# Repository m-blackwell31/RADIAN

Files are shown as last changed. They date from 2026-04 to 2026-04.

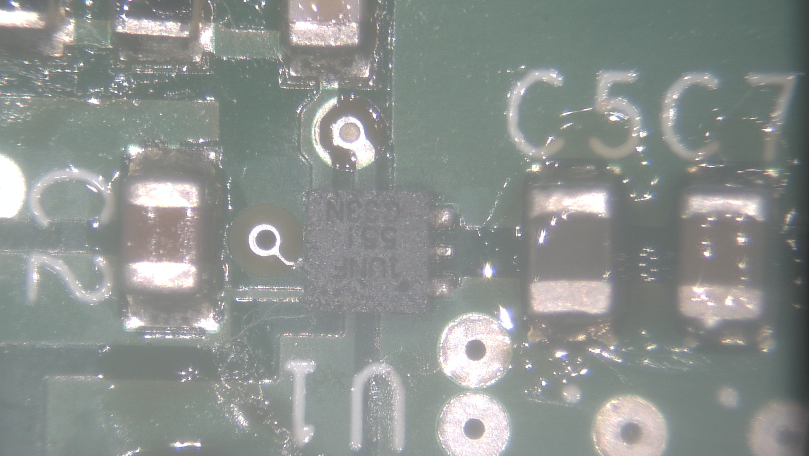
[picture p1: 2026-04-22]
GoogleDrive/physical/power_system/Solder Inspection/IMG00004.JPG

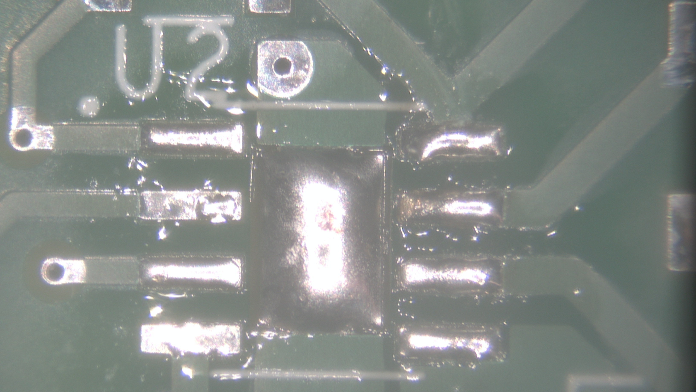
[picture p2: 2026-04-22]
GoogleDrive/physical/power_system/Solderability/IMG00003.JPG

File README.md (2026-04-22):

# RADIAN — Radar-Based Fall Detection System

## Overview

RADIAN is a human fall detection system developed for the Texas A&M University ECEN 403/404 Capstone Course. The system uses a mmWave radar sensor combined with machine learning algorithms to detect falls in real time and alert caregivers via a mobile app notification.

---

## Repository Structure

```
/RADIAN
├── fall_detector/        # ML models (.pkl), fall detector scripts, training code
├── MobileApp/            # Flutter/Dart app (Gotify alerts, fall log, login screen)
├── RADIAN_Data/          # mmWave data collection, CNN model, radar testing scripts
├── RADIAN_Physical/      # PCB design (Altium), CAD enclosure, power system docs
├── RADIAN_Radar/         # AWR6843ISK config (config3.cfg), mmwave_run6.py, requirements
└── GoogleDrive/          # Project documentation, presentations, and reports
    ├── docs/             # FSR, ICD, ConOps, final report, validation plan, budget
    ├── presentations/    # All 403 and 404 status update and demo presentations
    ├── data/             # Demo videos, pipeline diagrams, ML documentation
    ├── physical/         # Power board validation, datasheets, solder inspection photos
    ├── wireless/         # Raw radar testing data (.ndjson files) — falls and non-falls
    └── logo/             # RADIAN logo
```

---

## System Description

RADIAN uses a Texas Instruments AWR6843ISK mmWave radar sensor mounted at an elevated position to monitor a room. Point cloud data is streamed over UART to a Raspberry Pi, where a trained ExtraTrees machine learning classifier determines in real time whether a fall has occurred. Upon detection, a buzzer (GPIO27) alerts locally, and a push notification is sent to the caregiver's mobile app via Gotify.

### Key Components

| Component | Description |
|---|---|
| TI AWR6843ISK | mmWave radar sensor |
| Raspberry Pi | Main compute module |
| AP64501 | Synchronous buck converter |
| MP2615 | Li-ion battery charger IC |
| S-8252AAO | 2-cell battery protection IC |
| 2S2P 7,000 mAh LiPo | Battery pack (~3h 45m runtime) |
| GPIO27 Buzzer | Local fall alert |
| Flutter Mobile App | Caregiver notification app |

---

## Team

**Texas A&M University — ECEN 403/404 Capstone, Spring 2026**
Team 60 — RADIAN

| Name | GitHub |
|---|---|
| Matthew Blackwell | m-blackwell31 |
| Wyatt Johnson | ANDYSALAD1 |
| Mitch Hoffman | hoffmanmitchell |

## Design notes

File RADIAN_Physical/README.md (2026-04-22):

# RADIAN — Physical Subsystem

## Overview

This directory contains all physical design files for the RADIAN fall detection system, including the enclosure, PCB mounting hardware, and battery/component layout. The physical subsystem houses the Raspberry Pi compute module, mmWave radar sensor, power electronics, and buzzer in a compact, mountable enclosure.

---

## Directory Structure

```
/physical
├── CAD/
│   ├── enclosure.SLDPRT         # SolidWorks enclosure part file
│   ├── enclosure.SLDASM         # SolidWorks assembly file
│   └── drawings/                # Exported engineering drawings (PDF)
├── PCB/
│   ├── RADIAN.PrjPcb            # Altium project file
│   ├── Schematics/              # Schematics
│   ├── RADIAN.PcbDoc            # Board layout
│   ├── BOM.xlsx                 # Bill of materials
│   └── Gerbers/                 # Fabrication output files
└── README.md
```

---

## Enclosure

- Designed in **SolidWorks**
- Houses the Raspberry Pi, mmWave sensor, battery pack, and power board
- Mounting features for PCB standoffs and sensor window cutout
- Export formats: `.SLDPRT`, `.SLDASM`, PDF drawings

---

## PCB Design

- Designed in **Altium Designer**
- Includes power regulation (buck converter), MP2615 battery charger, and S-8252 protection IC 
- Battery: 2S2P 7,000 mAh LiPo pack (~3h 45m runtime under ~1,500 mA load)

### Key Components

| Component | Description |
|---|---|
| MP2615 | Battery charger IC |
| AP64501SP-1 | Buck Converter |
| S-8252 | Protection IC

---

## Tools Required

- SolidWorks 2022 or later (CAD files)
- Altium Designer (PCB files)
- Standard PCB assembly tools (soldering station, multimeter, calipers)

---

## Team

**Texas A&M University — ECEN 404 Capstone**  
RADIAN Fall Detection System  
Spring 2026

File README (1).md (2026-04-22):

# RADIAN — Radar-Based Fall Detection System

## Overview

RADIAN is a human fall detection system developed by Team 60 for the Texas A&M University ECEN 403/404 Capstone Program. The system uses a mmWave radar sensor combined with machine learning algorithms to detect falls in real time and alert caregivers via a mobile app notification.

---

## Repository Structure

```
/RADIAN
├── fall_detector/        # ML model and fall detection algorithms (Python)
├── MobileApp/            # Flutter/Dart mobile app for caregiver alerts
├── RADIAN_Data/          # Radar data collection scripts and mmWave run files
├── RADIAN_Physical/      # PCB design (Altium), CAD enclosure, power system
├── RADIAN_Radar/         # Radar configuration files and sensor interface code
└── GoogleDrive/          # Project documentation, presentations, and reports
    ├── docs/             # FSR, ICD, ConOps, final report, validation plan
    ├── presentations/    # All 403 and 404 presentations
    ├── data/             # Demo videos, diagrams, ML documentation
    ├── physical/         # Power board validation, datasheets, solder inspection
    ├── wireless/         # Radar testing data (.ndjson files)
    └── logo/             # RADIAN branding assets
```

---

## System Description

RADIAN uses a Texas Instruments AWR6843ISK mmWave radar sensor mounted at an elevated position to monitor a room. Point cloud data is streamed over UART to a Raspberry Pi, where a trained ExtraTrees machine learning classifier determines in real time whether a fall has occurred. Upon detection, a buzzer (GPIO27) alerts locally and a push notification is sent to the caregiver's mobile app via Gotify.

### Key Components

| Component | Description |
|---|---|
| TI AWR6843ISK | mmWave radar sensor |
| Raspberry Pi | Main compute module |
| AP64501 | Synchronous buck converter |
| MP2615 | Li-ion battery charger IC |
| S-8252AAO | 2-cell battery protection IC |
| 2S2P 7,000 mAh LiPo | Battery pack (~3h 45m runtime) |
| GPIO27 Buzzer | Local fall alert |
| Flutter Mobile App | Caregiver notification app |

---

## Getting Started

### Running the Fall Detector

SSH into the Raspberry Pi and run:

```bash
timeout 15 python3 mmwave_run6.py
```

The fall detector runs automatically on boot as a systemd service.

### Mobile App

See the `/MobileApp` directory for setup and build instructions.

---

## Team

**Texas A&M University — ECEN 403/404 Capstone, Spring 2026**
Team 60 — RADIAN Fall Detection System

| Name | GitHub |
|---|---|
| Matthew Blackwell | m-blackwell31 |
| Wyatt Johnson | ANDYSALAD1 |
| Mitch Hoffman | hoffmanmitchell |
| wyattjohnson-a1ly | wyattjohnson-a1ly |

---

## Instructors & Access

This repository is shared with:
- `kjnowka`
- `pranav-d1993`
- `johnlusher`
- `skalafatis`

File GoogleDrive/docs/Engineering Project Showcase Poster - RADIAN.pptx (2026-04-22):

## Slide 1

The RADIAN System
Matthew Blackwell, Mitchell Hoffman, & Wyatt Johnson
Dr. Ayra Menon

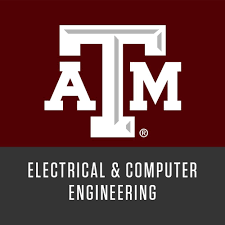
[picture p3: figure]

Problem Definition
Falls are the leading cause of injury in elderly individuals. Many current COTS systems are invasive, such as a camera, or require user input, such as a life-alert press or donning a smart device. RADIAN attempts to solve these challenges through a radar-based system and a machine learning model.

Design
The RADIAN system is broken up into 3 separate systems to solve the challenges present with current fall detection solutions. The RADIAN system will automatically detect falls in real time with minimal user input, preserve privacy, and send an immediate and accurate notification alert to caregivers.
Physical
- Power distribution and charging
- Enclosure and stand
- System Pipeline
Data
- Machine Learning model (ExpertTrees)
- Sending notification to Gotify Server
- System Pipeline
Wireless
- Radar configuration and parsing
- Setting up Gotify Server
- RADIAN Application on personal device

Engineering Analysis
Model Performance:
Through meticulous training, testing, retraining, and validation, the RADIAN team was able to create a model that had:
Precision at 0.96, Recall at 0.99, and Accuracy at 0.98 at a threshold of 0.48

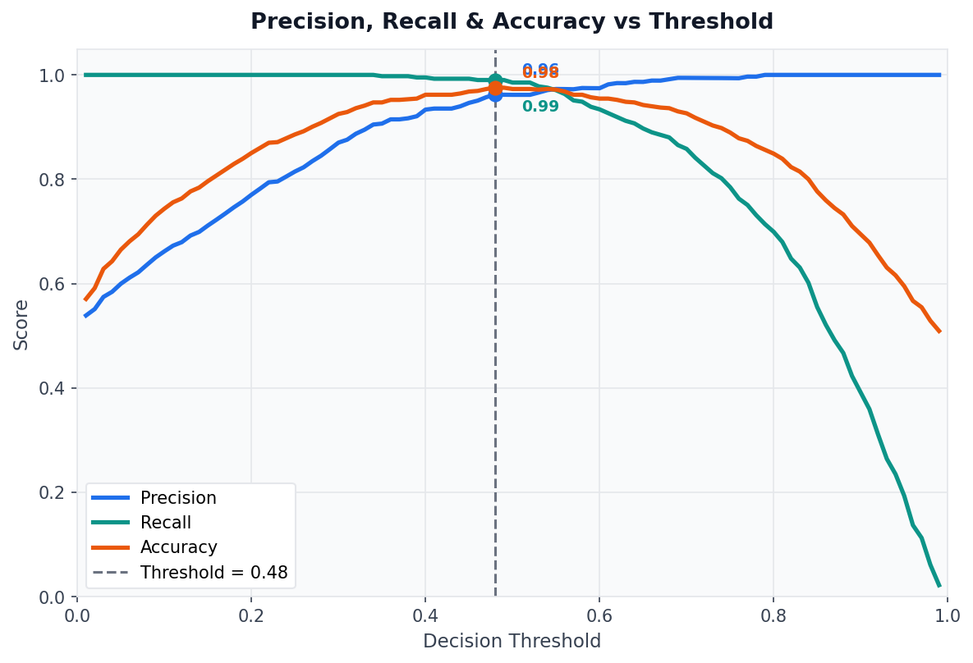
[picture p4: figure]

Figure 2. Graph of Precision, Accuracy, and Recall

Threshold Tradeoff:
The RADIAN team found that a threshold of 0.90 led to fewer false positives, but struggled to detect falls overall. They found that a threshold of 0.48 led to better fall detection, but many more false positives, leading to the chosen 0.70 threshold.

Key Features:
Z-height features were the strongest predictors in the RADIAN ML model, where falls are characterized by a rapid decrease in vertical body position. Point density is also heavily considered, where the number of points changes during a fall, indicating body compression and posture change. Velocity features were less dominant, showing that the model learned that motion alone does not constitute a fall. Overall, the model relies more on spatial posture changes than on motion alone, aligning with the physical characteristics of a fall.

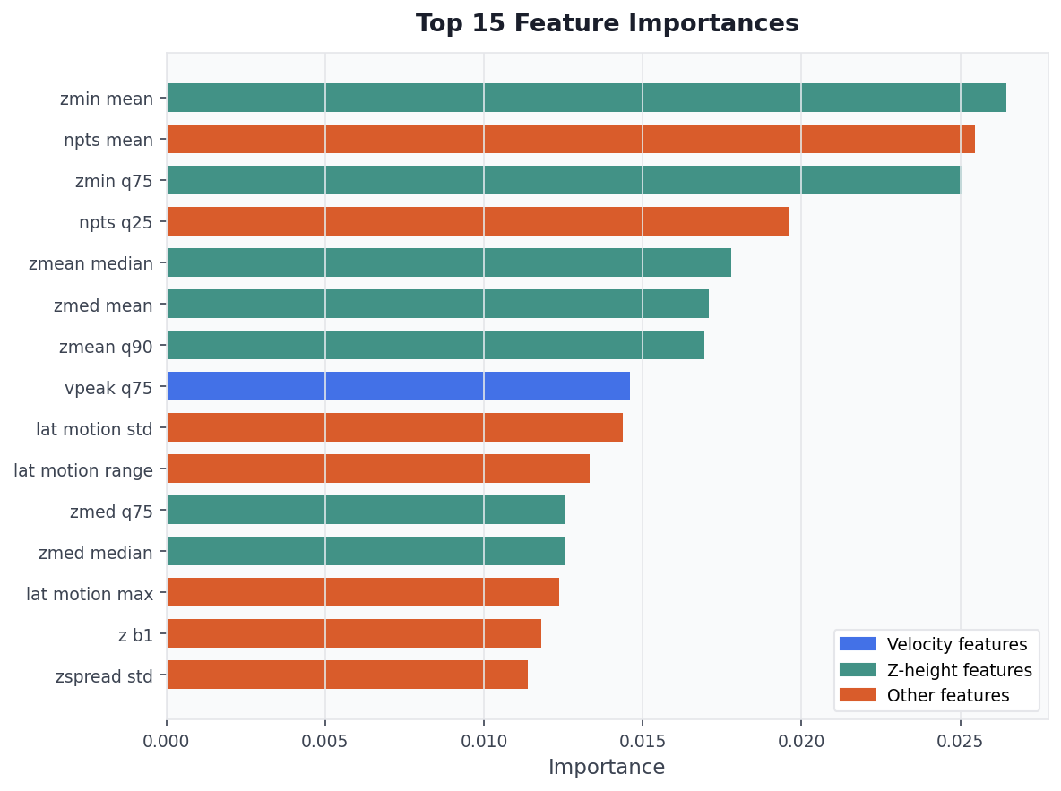
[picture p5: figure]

Figure 3. Graph of Top 15 Feature Importances

Outcomes
Achieved real-time fall detection, with a real-world fall accuracy of ~75% and an alert rate of 100% within 1 second at any range.

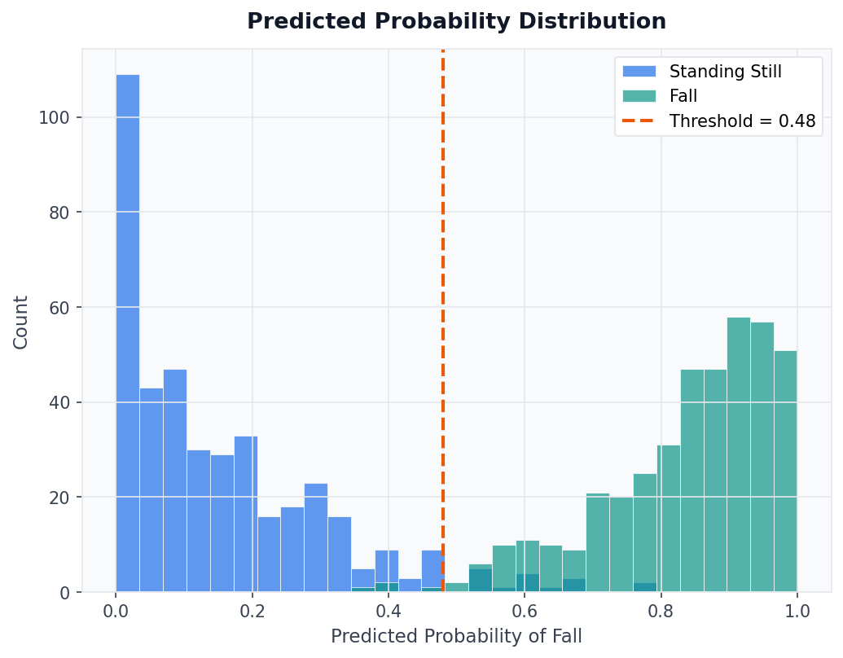
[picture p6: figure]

FIGURE HERE

Figure 4. Fall vs. Non-Fall Probability Distribution

The RADIAN system is a student-designed non-invasive, privacy-preserving solution that eliminates the need for cameras or wearable devices.

Impact
The RADIAN system provides peace of mind for elderly individuals and their families by ensuring rapid response in the event of a fall. Through this design, the RADIAN team
- Provides a scalable solution that can be deployed in homes, assisted living facilities, and hospitals
- Reduces response time to falls, allowing the caregivers to be notified immediately and potentially preventing serious injury
- Demonstrates the viability of the combination of radar-based sensing and machine learning for real-world healthcare applications

mmWave Radar
TI AWR6843ISK

UART Parser
Point cloud decode and Clustering

Feature Extraction
289 features including z-drop and v-spike

1

2

3

4

5

ML Inference
ExtraTrees, Sliding Window, and 32 FPS

Alert System
GPIO Buzzer, Gotify push notifications, CSV Logging

Figure 4. System-level Pipeline Diagram

- Implemented real-time detection pipeline, processing radar data and triggering alerts with minimal latency
- Developed a fully functional radar-based fall detection system integrating sensing, machine learning, and wireless communication
- Successfully differentiated falls from normal activities such as walking, sitting and standing using spatial and statistical features.

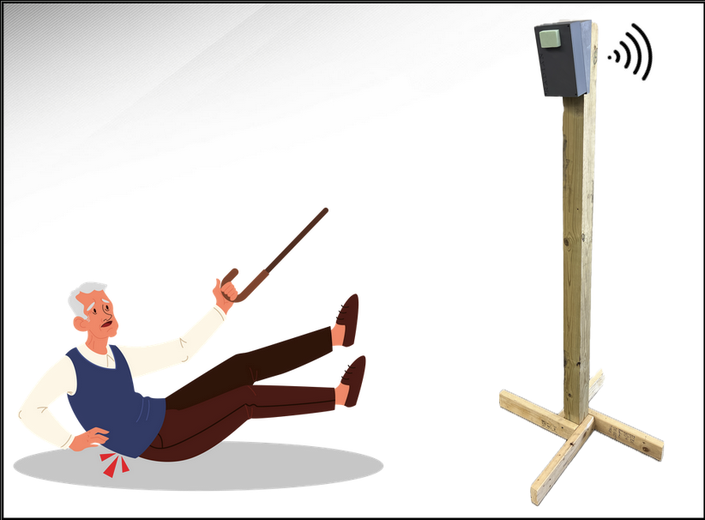
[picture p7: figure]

Figure 1. Full System Diagram

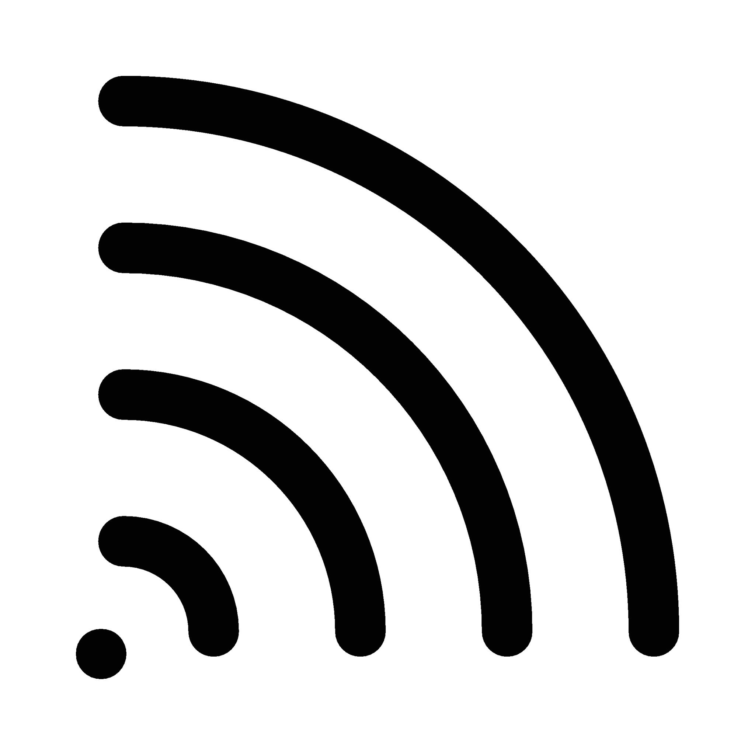
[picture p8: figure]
signal (Provided by Getty Images)
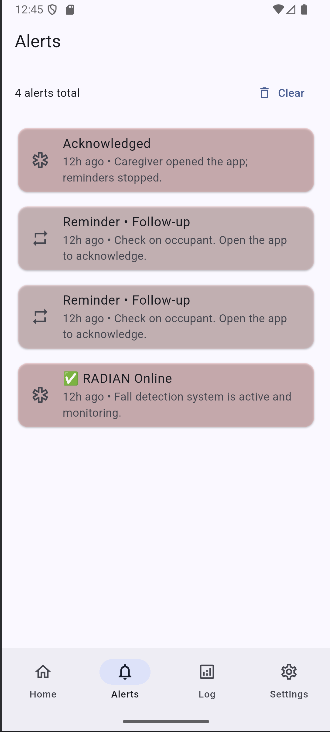
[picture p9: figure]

References
1. TI AWR6843ISK mmWave Sensor Datasheet, Texas Instruments, 2021
2. Pedregosa et al., "Scikit-learn: Machine Learning in Python," JMLR, 2011
3. Gotify Server Documentation, gotify.net
4. TI mmWave SDK User Guide, Texas Instruments, 2021
5. Raspberry Pi 3 Model B+ Specifications, Raspberry Pi Foundation

Acknowledgements
The RADIAN team would like to thank Dr. Ayra Menon, Roman Venagas, and Manoj Kumar Balamurugan for their guidance throughout this project, as well as the Texas A&M Department of Electrical and Computer Engineering for providing lab resources and support.

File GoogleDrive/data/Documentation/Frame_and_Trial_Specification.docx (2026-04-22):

RADIAN - RADar-based Intelligent Activity moNitoring

Matthew Blackwell

Mitch Hoffman

Wyatt Johnson

Frame & Trial Specification

Frame & Trial Specification

for

RADIAN

Team 60

Approved by:

_____________________________

Matthew Blackwell Date

Change Record

Rev. | Date | Originator | Approvals | Description
1 | 01/29/2026 | Matthew Blackwell | | Draft Release

Table of Contents

1. Introduction 7

1.1. Purpose 7

1.2. System Overview 7

1.3. Defintions 7

2. Frame and Data Structure 7

2.1. Metadata 7

2.2. Center of Mass Data 7

3. Trial Structure 8

3.1. Trial Length 8

4. Dataset Organization 9

4.1. Folder Structure 9

4.2. Units and Coordinate Conversions 9

5. Assumptions and Limitations 9

6. Example Data 9

List of Tables

List of Figures

# 1. Introduction

## 1.1. Purpose

The purpose of this document is to define the official data format for the RADIAN radar-based motion detection and fall detection trials. This will ensure that the data is consistent, reproducible, and usable for the Data subsystem’s algorithm development and machine learning. This specification is frozen for the initial trials, and future extensions must remain backwards-compatible.

## 1.2. System Overview

The sensor type is a radar-based human detection system using Wireless’s TI board to receive the radar data. The output rate is ____. The primary task of the machine learning algorithm is to classify human motion correctly and accurately, including but not limited to standing, walking, sitting, and falling. The target for running the ML algorithm is a Raspberry Pi 3, specifically running a 1D CNN model.

## 1.3. Defintions

This section will go over a few definitions needed to understand the use of this document.

Frame: A single radar snapshot at one timestamp, producing a detected center of mass.

Trial: A sequence of consecutive frames representing one continuous human action and is assigned a single class label.

Timestep: One timestep corresponds to one frame

# 2. Frame and Data Structure

Each of the frames must contain each of the following fields

## 2.1. Metadata

- frame_id (int): Monotonically increasing frame index
- timestamp (float): Time in seconds since the trial start

## 2.2. Center of Mass Data

- x_c (float): Center of mass position in the x-axis (meters)
- y_c (float): Center of mass position in the y-axis (meters)
- z_c (float): Center of mass position in the z-axis (meters)
  2.3. Center Tracking Rule

If the center of mass cannot be reliably detected in a given frame, then the most recent valid (x_c, y_c, z_c) value shall be reused. This event may be flagged internally, but will not invalidate the frame.

  2.4. Derived Frame-Level Features

These features are going to be specifically computed numerically from consecutive frames. Derived features are optional to store but must be computable from stored data.

    2.4.1. Velocity Components
- v_x = dx_c / dt
- v_y = dy_c / dt
- v_z = dz_c / dt
    2.4.2. Speed Magnitude
- |v| = sqrt(v_x^2 + v_y^2 + v_z^2)

# 3. Trial Structure

## 3.1. Trial Length

A trial will consist of 100 consecutive frames or roughly 10 seconds of data (N = 10 frames per second)

  3.2. Trial Label

Each trial is assigned exactly one label:

- Standing
- Walking
- Sitting
- Crawling
- Falling
- Other (Add on later)
  3.3. Trial Boundaries

A trial will begin:

- At the start of a movement or posture

A trial will end:

- When the action completes or transitions into another class

# 4. Dataset Organization

## 4.1. Folder Structure

The folder will be structured in this format:

data/

standing/

sitting/

walking/

crawling/

falling/

## 4.2. Units and Coordinate Conversions

Distance will be measured in meters (m). Time will be measured in seconds (s). Velocity will be measured in meters per second (m/s). To coordinate the frame origin and orientation, it will be defined by the radar mounting configuration.

# 5. Assumptions and Limitations

Only a single human is tracked per frame and will not have any other human shaped objects in the room. Occlusions may cause a temporary center reuse. Fine-grained posture details will not be captured at the frame level, at least with the data directly given from the radar

# 6. Example Data

Below is an example of a single frame stored in JSON format. This represents one timestamp of radar data:

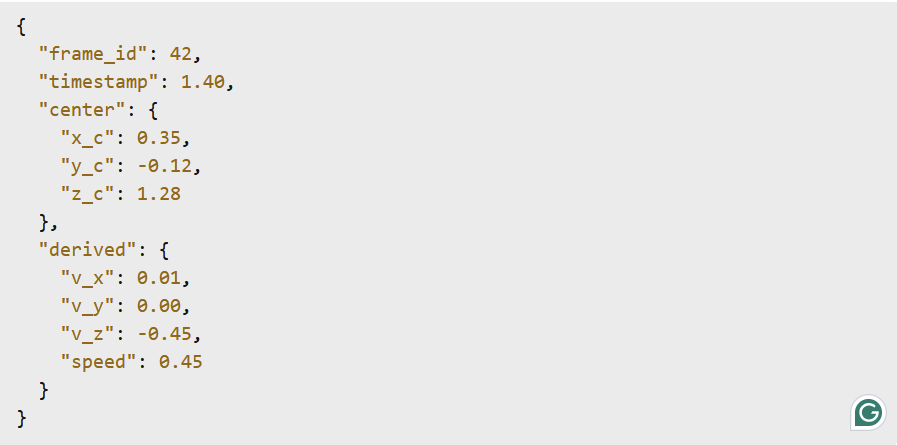
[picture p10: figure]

Notes:

- Positions are given in meters
- Velocities are computed using finite differences between consecutive frames
- Negative v_z indicates a downward motion

Below is an example of a complete trial consisting of multiple frames and a single label:

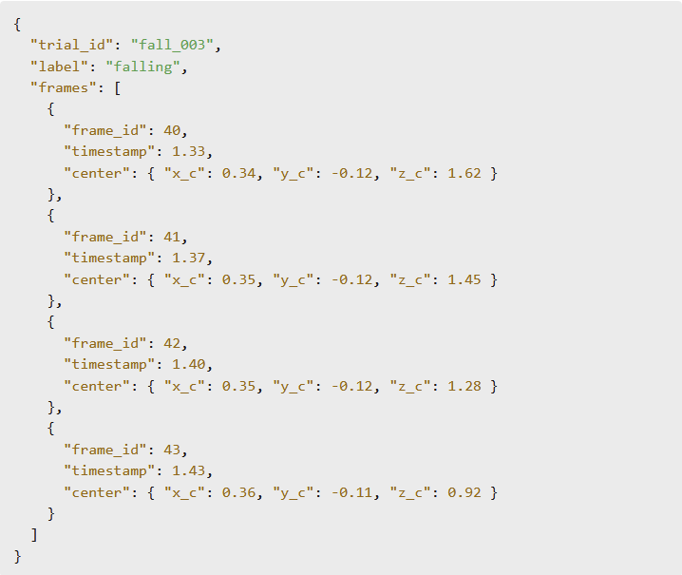
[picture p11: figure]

Notes:

- All frames in a trial are consectutive in time
- A single label applies to the entire trial
- Derived features may be stored per frame or computed during preprocessing

Data Frame Format Revision - 1 RADIAN

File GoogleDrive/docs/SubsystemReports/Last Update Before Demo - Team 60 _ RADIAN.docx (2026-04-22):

Data Update (Matthew Blackwell):

Overall, the subsystem is acting as expected. Using a random forest ML model, I am using the ML model to determine if a point is static or dynamic. Initially, I had the model only classify based on velocities provided by the radar (thus making the ML model redundant). However, I have since updated the model to include AWGN, jitter, slight movements, sudden movements, and other realistic attributes that could be received from our wireless subsystem. While I believe this to be robust enough for the demo for the end of 403 (and where I can continue to improve in 404), my lack of ML knowledge could prove that my model currently is not robust enough to prove subsystem successes. Over the next week, I will be adding validation testing through “false positives”, such as sitting, bending over, falling and catching oneself, etc, to show that my system will work as intended. I will also expand the model to include more training data to ensure that it is accurate and simulates the numerous data points that will eventually be generated by the radar.

Overall, my only concern with the Data subsystem is that the model is not robust enough for the expectations of the subsystem. I believe that it will work for what I am using it for and will pass the validation testing I have planned.

Wireless Update (Mitchell Hoffman):

The wireless subsystem consists of radar data processing, UART communication to the Raspberry Pi within the Data subsystem, and an Android based mobile application for caregivers. For the radar component, I developed a Python pipeline that configures the AWR6843ISK using a custom TI generated configuration file, receives the binary stream over UART, parses the TLV frames, and outputs a point cloud containing x, y, z, and velocity data. The mobile app was developed in Flutter and is implemented for Android.. The app uses a tab based UI, has been tested fully in Android Studio, and can receive simulated fall alerts. While Flutter supports iOS, the app has only been tested on Android due to available development resources. Both the radar processing and mobile app can function independently. The remaining work that needs to be done on the radar is to test it in different scenarios, especially edge cases. As far as the mobile app the remaining work to be done is to test the communication to the Gotify server, and if it can receive dummy alerts and correctly present those alerts within each tab.

Physical Update (Wyatt Johnson):

The RADIAN power subsystem is comprised of a PCB board that uses two parallel Li-ion batteries to provide power to a Raspberry Pi and mmWave radar. The PCB has a linear charging chip (TP4056 with the battery negative tied to ground), a battery protection circuit, and a boost circuit using a TI integrated circuit. Currently, the PCB is capable of powering a Raspberry Pi, and testing with the radar has not been done yet due to not wanting to damage another member’s subsystem. The power board can power the Raspberry Pi with about a 0.1 V drop on the 5 V rail. The charging circuit has been verified to increase the Li-ion batteries smoothly from ~3.5 V with no heating issues. I have not yet completed a full battery-only runtime test with the final RADIAN load to fully characterize charge time or undervoltage cut-off behavior. We have not done worst-case scenarios, such as worst-case load or deliberate short-circuit or over-current faults, due to not wanting to potentially cause components to be damaged. A future revision is planned to include a power-path charger and improve layout and protections, but the current power PCB is functional and capable of supporting the RADIAN devices.

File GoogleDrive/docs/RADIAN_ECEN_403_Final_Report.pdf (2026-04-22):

# RADIAN - RADar-based Intelligent Activity moNitoring

# Matthew Blackwell Mitch Hoffman Wyatt Johnson

## CONCEPT OF OPERATIONS

CONCEPT OF OPERATIONS

FOR

## RADIAN

TEAM 60

APPROVED BY:

_____________________________
Matthew Blackwell | Date

_____________________________
Prof. Jang | Date

_____________________________
Roman Venegas | Date

Concept of Operations | Revision - 4
RADIAN

### Change Record

Rev . | Date | Originator | Approvals | Description
1 | 09/09/25 | Matthew Blackwell | | Baseline Release
2 | 09/20/25 | Matthew Blackwell | | Microcontroller Switch
3 | 10/04/25 | Matthew Blackwell | | MCU removal, SMS removal, and other edits from ICD
4 | 12/05/25 | Wyatt Johnson | | Document formating

Concept of Operations | Revision - 4

## Table of Contents

Table of Contents | 3
List of Figures | 4
1. Executive Summary | 5
2. Introduction | 6
2.1. Background | 6
2.2. Overview | 6
2.3. Referenced Documents and Standards | 6
3. Operating Concept | 8
3.1. Scope | 8
3.2. Operational Description and Constraints | 8
3.3. System Description | 8
3.3.1. Physical Design | 8
3.3.2. Wireless Design | 9
3.3.3. Data Design | 9
3.4. Modes of Operations | 9
3.5. Users | 9
3.6. Support | 10
4. Scenario(s) | 11
4.1. Fall Detection | 11
4.2. Normal Activity Monitoring | 11
4.3. Multi-Room Monitoring | 11
5. Analysis | 12
5.1. Summary of Proposed Improvements | 12
5.2. Disadvantages and Limitations | 12
5.3. Alternatives | 12
5.4. Impact | 12

Concept of Operations | Revision - 4

## List of Figures

Concept of Operations | Revision - 4

## 1. Executive Summary

Falls are a leading cause of injury among elderly individuals, often resulting in severe health consequences. Existing monitoring solutions on the market, such as wearable devices and camera-based systems, suffer from significant drawbacks. Wearable devices rely on user compliance, and camera-based systems compromise privacy. To address these drawbacks, this project proposes the development of a low-cost, AI-enabled fall detection system using a millimeter wave (mmWave) radar marketed for the elderly at risk of falls.

The RADIAN system uses a commercially available mmWave radar sensor to continuously monitor human activity within an indoor environment, such as a living room or bedroom. The use of mmWave technology allows for privacy to be preserved while still providing adequate protection. The data from the radar will be processed through an embedded microcontroller on the mmWave Radar board and then passed to a Raspberry Pi, where AI algorithms will classify motion patterns to detect falls. In the event of a fall, the RADIAN system will automatically send a wireless alert to a caregiver’s smartphone via Wi-Fi, as well as set off an alarm on the device itself to alert anyone inside the house. The budget approved for the RADIAN group is $375, keeping the project low-cost.

Concept of Operations | Revision - 4

## 2. Introduction

The RADIAN (RADar-based Intelligent Activity moNitoring) system will detect human falls within an enclosed space, specifically in a household or office setting, using radar-based systems. The RADIAN system will detect a fall using AI-based machine learning algorithms and send an alert to a cellular device, ensuring that the fall is caught quickly and accurately.

### 2.1. Background

The leading cause of injury-related death among adults ages 65 and older is falls [1]. Many current solutions rely on vision-based systems or a wearable device, both of which suffer from limitations such as user compliance, privacy concerns, and coverage gaps. A millimeter-wave radar preserves privacy, a non-contact, and reliable means of monitoring human activity indoors.

### 2.2. Overview

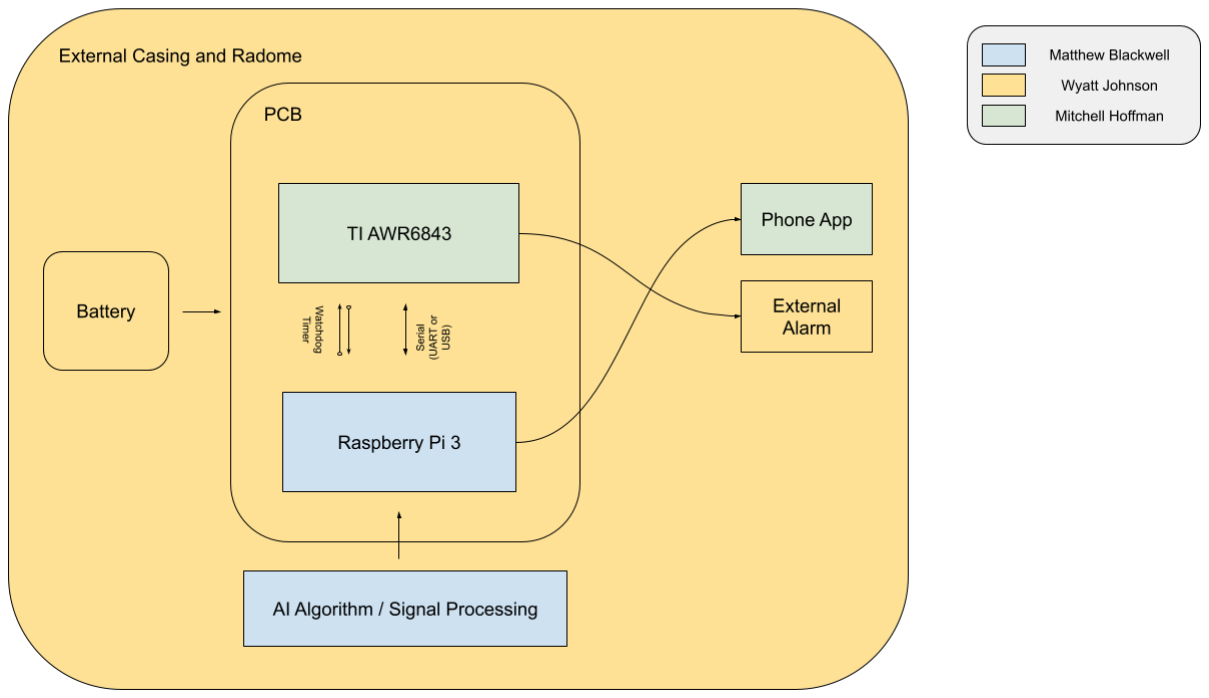
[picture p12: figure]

Figure 1: High-Level Block Diagram for RADIAN system

A mmWave Radar Sensor will be used to monitor human movement in a room. Data from the radar is processed using AI algorithms to detect falls in real time. Once a fall is detected, the device will activate an alarm as well as send a remote wireless notification to a mobile device via Wi-Fi.

### 2.3. Referenced Documents and Standards

- IEEE 802.11 Wi-Fi standards

Concept of Operations | Revision - 4
- IEEE 802.15.4 for wireless communications
- IEEE 521-2002 Standard Letter Designations for Radar-Frequency Bands
[1] “Falls Data & Research.” Centers for Disease Control and Prevention, Accessed at https://www.cdc.gov/falls/data-research/index.html#:~:text=Deaths%20from%20older%20adult%20falls,.cdc.gov/STEAD

Concept of Operations | Revision - 4

## 3. Operating Concept

### 3.1. Scope

The RADar-based Intelligent Activity moNitoring (RADIAN) system is designed to enhance the safety of elderly and physically disabled individuals by providing timely alerts in the event of a fall within a monitored room. Once installed, the RADIAN system will continually monitor a closed room for human presence and movement. Fall events are identified by an in-house-developed artificial intelligence (AI) and machine learning algorithm, based on extensive testing by the RADIAN group. When the AI determines that a fall has occurred, a wireless signal will transmit to a dedicated mobile application developed by the RADIAN group, alerting those most important to the monitored individual. In addition, there will be an audible alarm system to alert those in the building to the fall. By combining real-time monitoring with reliable alerting mechanisms, the RADIAN system allows for peace of mind for at-risk individuals and their families.

### 3.2. Operational Description and Constraints

The RADIAN system is designed to be used in closed rooms of varying sizes, both in room area and ceiling height. The RADIAN system is designed to be relatively easy to use for the user, both in the setup of the radar as well as the alert system and its GUI. A RADIAN system will be set up in the corner of a room, with the sensor and radome facing down at a 45° angle to ensure that the RADIAN system is scanning the entire room. The GUI (Graphical User Interface) will ask what room the RADIAN system is set up in to organize each RADIAN system and to understand what furniture and other objects could be scanned. As the RADIAN system scans the room, the raw data will be processed through the microcontroller embedded in the RADIAN system and then sent to an AI algorithm to analyze the room. If the AI detects a fall, then a signal will be sent to the microcontroller to then alert the GUI that a fall was detected through an app notification.

Here are the resulting constraints of the RADIAN system for it to operate properly according to the description:
- The RADIAN system must not be blocked by any object
- The RADIAN system has to be placed in a high vantage point at a 45° downward angle
- The RADIAN system’s radome must be directed towards the largest area of the room
- The RADIAN system must be powered via battery
- The RADIAN system must be small in size (e.g., wall-mountable, no larger than a shoebox) to ensure user-friendliness during installation, thus limiting the complexity of parts that can be used
- The RADIAN group has a budget of $375, further constraining the complexity of the RADIAN system

### 3.3. System Description

### 3.3.1. Physical Design

The radar board, which includes a TI AWR6842ISK and a Raspberry Pi, will all be connected to the battery system on a custom-designed PCB (Printed Circuit Board)

Concept of Operations | Revision - 4

designed in-house by the RADIAN group. This PCB design will enhance the RADIAN system's reliability during installation, as no components can be removed. The RADIAN group will also study and implement the power management in this subsystem, ensuring that the correct voltage and current are being provided to the various components of the RADIAN system. The battery casing will also be screwed to the board and include a removable housing and leads to facilitate battery replacement when needed, ensuring the continued reliability of the RADIAN system.

### 3.3.2. Wireless Design

The radar chip will be hand-selected through thorough research and trade studies by the RADIAN group to guarantee reliability and affordability for the consumer and users of the RADIAN system. The TI radar board will be programmed to collect the raw data from the radar chip and convert it into usable data for the AI algorithm stored on the Raspberry Pi. Once the AI algorithm has detected a fall, a signal will be sent to an external alarm connected to the RADIAN system. The wireless design subsystem will also be responsible for the application's GUI, providing both a frontend and a backend to ensure that the application is easy to use and runs smoothly.

### 3.3.3. Data Design

The AI algorithm is the primary focus of the data subsystem, utilizing a simple AI model developed by the RADIAN group to predict fall occurrences. The RADIAN group will do extensive testing and training of the AI model to ensure that false positives and true negatives do not send alerts. The application may have various options to select where the RADIAN system is placed, to help the AI algorithm understand what objects may or may not be in a room. Some examples include a bed present in a bedroom, but not in a living or dining room. Having these distinctions allows for fewer false alarms when the user is lying down vs. falling. The data subsystem will also be responsible for communicating with the cloud server to send the push notifications. A wireless Wi-Fi communication will be sent from the Raspberry Pi 3 to the Gotify cloud to alert those not in proximity of the audible alarm using the RADIAN phone application.

### 3.4. Modes of Operations

The RADIAN system will only have one operating mode, as the radar has to constantly sweep a room due to the random nature of human movements. Within this mode, the user will be able to define what room the RADIAN system is placed in to aid the AI algorithm in understanding what may or may not be in the room. When operating in the mode, the radar will constantly detect the room and the objects around the room, sensing for motion and a potential fall. If a fall is detected by the RADIAN system and its AI algorithm, then an alert will be sent to the desired device, as well as set off an audible alarm for those in proximity.

### 3.5. Users

The RADIAN system will be marketed to the high-risk individuals who greatly benefit from a fall detection system in their home without having to worry about privacy infringement with camera-based detection systems. Our product will allow users and their loved ones to have peace of mind when it comes to the health and safety of the user.

Concept of Operations | Revision - 4

The RADIAN system can also double as a simple motion detection device that can be used in various security applications, including home security, business security, and preventing deaths in the back of motor vehicles.

### 3.6. Support

The RADIAN group will provide an extensive manual detailing the installation of the RADIAN system, battery replacement, and a simple explanation of how the RADIAN system works at the highest level. Within the RADIAN application, detailed step-by-step guides will be provided to guide the user through the setup and operation of the device.

Concept of Operations | Revision - 4

## 4. Scenario(s)

### 4.1. Fall Detection

An elderly person falls in their bedroom or living room. The RADIAN system will use mmWave radar technology to record and process the elderly person's fall. This mmWave radar data will then be sent to an AI model that will then classify the event as a fall, triggering an alarm and notifying the caretaker. This notification will be sent to a caregiver's smartphone through an app. The caregiver will then be able to check on the individual quickly and allow for the necessary response as soon as possible.

### 4.2. Normal Activity Monitoring

The RADIAN system user can be walking, sitting, or lying down in their bedroom. The radar will detect all of these events, but the AI model will classify these events as “safe”. No alerts will be sent in these events, and will allow the user to continuously monitor their environment for hazardous falls without invading their privacy.

### 4.3. Multi-Room Monitoring

The user is capable of monitoring a whole house or a nursing home. The user will install multiple RADIAN systems in each room that they would like to monitor. Each RADIAN system will individually monitor the room in which it is. If the RADIAN system detects a fall, it will notify the caregiver of the event and also provide the location of the room in which it occurred. While one room is triggered, the other rooms will be continuously monitored. All of the data from the rooms can be examined in the RADIAN smartphone app by the caregiver, providing complete protection of the whole building.

Concept of Operations | Revision - 4

## 5. Analysis

### 5.1. Summary of Proposed Improvements

The RADIAN system will be battery-powered, providing wireless capabilities and flexible placement without requiring a constant wired connection. The radar subsystem will monitor human activity without capturing images, which allows for the protection of the privacy of users while still detecting falls. The AI model constantly monitors the radar subsystem’s data to detect falls and then sends notifications. Alerts will be sent directly to the caregivers or emergency responders, allowing for a quick response time to accidents. The RADIAN system will operate autonomously, allowing users to have minimal interaction with the device.

### 5.2. Disadvantages and Limitations

Due to the limited power, since it will be battery-powered, this can restrict our complexity for our AI algorithm, which could lead to false alarms and/or missing scenarios that should trigger the alarm. Depending on the mmWave radar settings and wireless communication frequency, this can cause the battery life to be significantly reduced. In complex environments (cluttered rooms, multiple people, animals, children), the RADIAN system could produce more false positives. Depending on the size of the room, the RADIAN systems may not be able to detect falls in the outer areas of a large room. For the RADIAN system to effectively communicate with emergency services, it will need to depend on reliable network connectivity.

### 5.3. Alternatives

PIR Motion Sensors are used for simple movement/presence detection, are cheap and easy to use, but can not detect falls. Camera-Based Monitoring can provide a visual view of the room and verify if a fall occurs, offers more data for an AI model and could be used to create a better model without the need for complex data or high-resolution cameras, but raises privacy concerns for bedrooms and living spaces and requires high processing power, and storage could be an issue, leading to a high price point. A wearable device is capable of detecting a fall with an onboard sensor and is more accurate with little complexity, but it requires the user to wear a device constantly, and it may be uncomfortable, or the user could forget to wear the device, making it not as reliable.

### 5.4. Impact

Environmental Impact: The RADIAN device has low energy consumption. Minimal waste since the device will be compacted.

Society Impact: Increases safety for the elderly by providing rapid fall detection without invading privacy. Reduces the response times for caregivers and/or emergency services. Enables the elderly to live independently without sacrificing safety.

Ethical concerns: Allows for privacy due to no audio or video recording

# RADIAN - RADar-based Intelligent Activity moNitoring

# Matthew Blackwell Mitch Hoffman Wyatt Johnson

## FUNCTIONAL SYSTEM REQUIREMENTS

FUNCTIONAL SYSTEM REQUIREMENTS

FOR

## RADIAN

TEAM 60

APPROVED BY:

_____________________________
Matthew Blackwell | Date

_____________________________
Prof. Jang | Date

_____________________________
Roman Venegas | Date

Functional System Requirements | Revision - 2

### Change Record

Rev . | Date | Originator | Approvals | Description
1 | 10/04/2025 | Matthew Blackwell | | Draft Release
2 | 12/05/2025 | Wyatt Johnson | | Document formatting

Functional System Requirements | Revision - 2

### Table of Contents

1. Introduction | 6
1.1. Purpose and Scope | 6
1.2. Responsibility and Change Authority | 6
2. Applicable and Reference Documents | 8
2.1. Applicable Documents | 8
2.2. Reference Documents | 8
2.3. Order of Precedence | 8
3. Requirements | 9
3.1. System Definition | 9
3.2. Characteristics | 10
3.2.1. Functional / Performance Requirements | 10
3.2.2. Physical Characteristics | 11
3.2.3. Electrical Characteristics | 12
3.2.4. Environmental Requirements | 13
4. Support Requirements | 14
4.1. Wi-Fi Connection | 14
4.2. Wi-Fi or Cellular Data Connection | 14
4.3. Battery Maintenance | 14
Appendix A: Acronyms and Abbreviations | 15

Functional System Requirements | Revision - 2

### List of Tables

Table 1: Subsystem Responsibility | 7
Table 2: Applicable Documents for the RADIAN System | 7
Table 3: Reference Documents for the RADIAN System | 7

Functional System Requirements | Revision - 2

### List of Figures

Figure 1: RADIAN Conceptual Image | 1
Figure 2. Block Diagram of Radian System | 4

Functional System Requirements | Revision - 2

## 1. Introduction

### 1.1. Purpose and Scope

Falls are a leading cause of injury among elderly individuals, often resulting in severe health consequences. Existing monitoring solutions on the market, such as wearable devices and camera-based systems, suffer from significant drawbacks. Wearable devices rely on user compliance, and camera-based systems compromise privacy. The RADIAN system will provide a low-cost, non-invasive, privacy-preserving fall detection system. The RADIAN system will use mmWave radar and AI algorithm technology to monitor human activity and detect falls in indoor environments, such as bedrooms and living rooms.

The RADIAN system will continuously monitor a room for motion patterns and classify them into fall/non-fall events in real time. Once a fall is detected, the RADIAN system will trigger an audible alarm and send a wireless alert to a caregiver’s smartphone. Figure 1 shows the RADIAN system that is proposed in CONOPS.

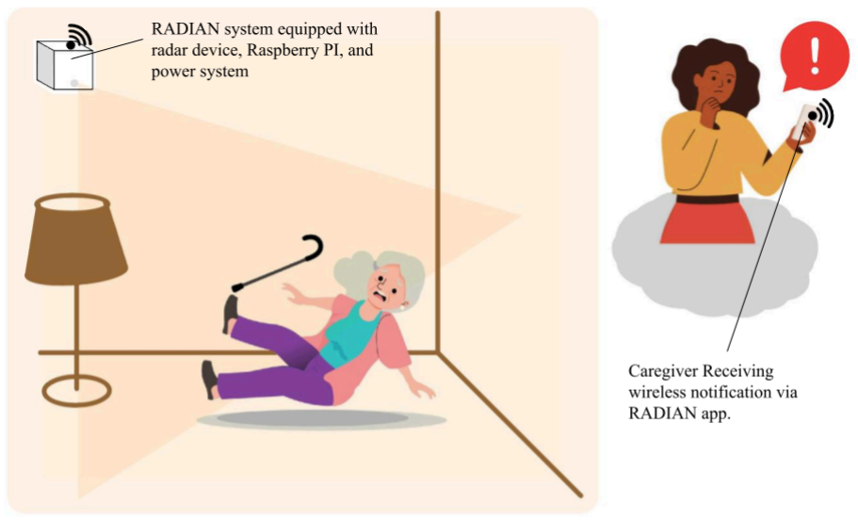
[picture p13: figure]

Figure 1: RADIAN Conceptual Image

This document describes detailed requirements for the RADIAN system, including the requirements for each subsystem (Physical, Wireless, and Data). The verification process for the RADIAN system will be described in a separate Validation Plan.

### 1.2. Responsibility and Change Authority

Matthew Blackwell, RADIAN’s team leader, will be responsible for ensuring that all requirements are met for the RADIAN system. These requirements can only be changed

Functional System Requirements | Revision - 2

with approval from Matthew Blackwell and Professor Arya Menon, the RADIAN faculty Contact.

Subsystem | Responsibility
AI Model and Communication | Matthew Blackwell
Radar Sensing and App Development | Mitchell Hoffman
Power System and Physical Enclosure | Wyatt Johnson
Table 1: Subsystem responsibility

Functional System Requirements | Revision - 2

## 2. Applicable and Reference Documents

### 2.1. Applicable Documents

The following documents, of the exact issue and revision shown, form a part of this specification to the extent specified herein:

Document Number | Revision/Release Date | Document Title
IPC/WHMA-A-620E | January 2022 | Requirements and Acceptance for Cable and Wire Harness Assemblies
UL 1977 | December 7, 2022 | Component Connectors for Use in Data, Signal, Control, and Power Applications
Table 2: Applicable Documents for the RADIAN System

### 2.2. Reference Documents

The following documents are reference documents utilized in the development of this specification. These documents do not form a part of this specification and are not controlled by their reference herein.

Document Number | Revision/Release Date | Document Title
IEEE 802.11 | Jan. 23, 1996 | IEEE Standard for Information Technology – Telecommunications and Information Exchange between Systems

Table 3: Reference Documents for the RADIAN System

### 2.3. Order of Precedence

In the event of a conflict between the text of this specification and an applicable document cited herein, the text of this specification takes precedence without any exceptions.

All specifications, standards, exhibits, drawings, or other documents that are invoked as “applicable” in this specification are incorporated as cited. All documents that are referred to within an applicable report are considered to be for guidance and information only, except ICD,s which have their relevant documents considered to be incorporated as cited.

Functional System Requirements | Revision - 2

## 3. Requirements

### 3.1. System Definition

The RADIAN system is an all-in-one, designed system to help protect the elderly and high-risk individuals with quick and accurate alerts when the user has fallen. This allows the caregiver, whether a health care professional or loved one, to feel comfort knowing that their loved one is safe. The RADIAN system will comprise three overarching subsystems, each with further design requirements that must be met for the RADIAN subsystem. These three subsystems include Physical, Data, and Wireless.

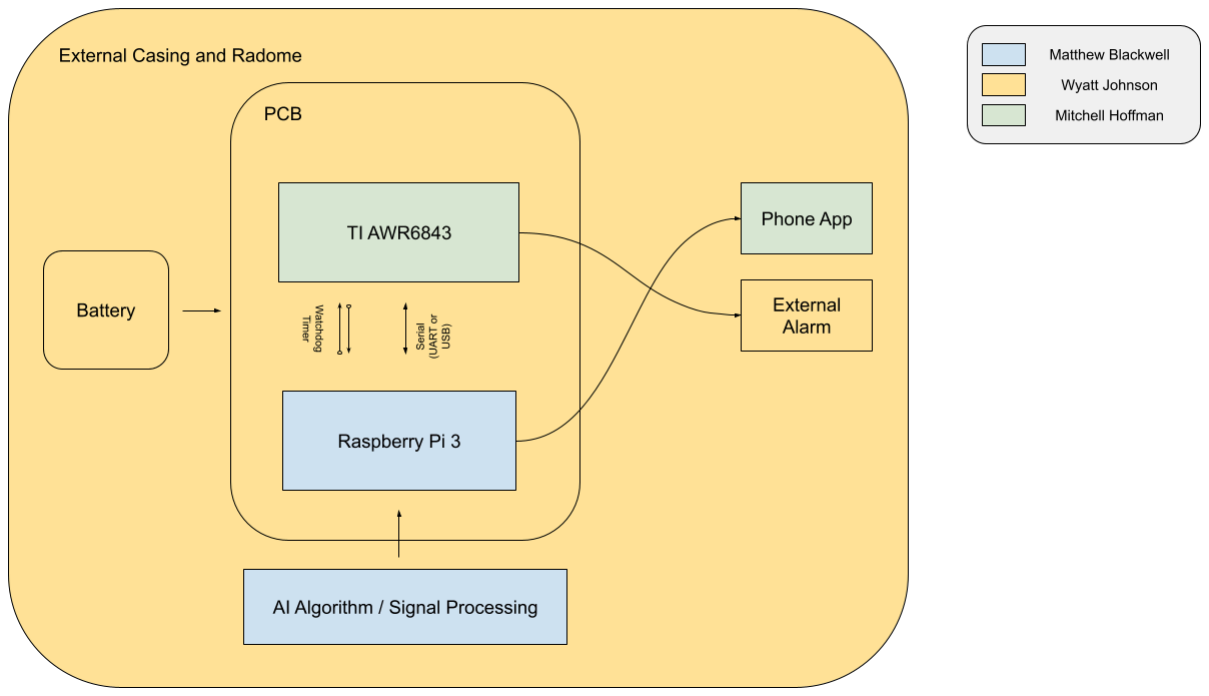
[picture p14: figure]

Figure 2. Block Diagram of Radian System

The entire RADIAN system is powered through two 3.7V rechargeable batteries, powering both the TI AWR6843ISK board and the Raspberry Pi 3, which are needed for the system to function. The rechargeable battery pack allows the user to easily charge the RADIAN system while maintaining maneuverability around the room. Both the TI board and Raspberry Pi 3 are connected to the custom-designed PCB, allowing for efficient connections and reduced risk of electrical connection failure between the subsystems. The ML model and AI algorithm are stored and run through the Raspberry Pi 3, where they will then communicate with an external phone application designed by the RADIAN group via a Gotify server. An external alarm will also be connected to the RADIAN system to alert anyone in the home while also alerting the caregiver’s device.

The RADIAN system may have a feature that will trigger a sleep mode on the Raspberry Pi 3 to conserve power when no motion is detected in the room. Once motion is detected of an elderly or high-risk individual, the radar will continuously scan the room, sending the

Functional System Requirements | Revision - 2

processed data to the Raspberry Pi 3. Through its AI algorithm and ML model, the Raspberry Pi 3 will be able to compute in real-time the position, velocity, acceleration, and other fall parameters of the individual. If the ML model decides that a true fall has occurred based on a variety of parameters and decisions, the Raspberry Pi will send a message. The Gotify server will receive this new message and create a WebSocket, allowing for the message to travel in real time to the phone application. The custom-designed application will then receive this message and send a push notification to the caregiver, alerting them of the fall.

By combining these three subsystems, RADIAN provides a portable, intelligent, and connected solution for fall detection, balancing energy efficiency with reliable caregiver communication.

### 3.2. Characteristics

### 3.2.1. Functional / Performance Requirements

### 3.2.1.1. Fall Detection Accuracy

The RADIAN system shall detect falls with a minimum of 90% accuracy under normal indoor conditions (room temperature, clear view of the falling subject, unobstructed view, within 5 meters).

Rationale: The system will need to have a high fall detection accuracy to verify its capabilities for detecting falls reliably, which will also increase user trust.

### 3.2.1.2. Detection latency

Once a fall is detected, the RADIAN system will send an alert and sound an alarm within five seconds of a fall.

Rationale: It is critical that caregivers or emergency responders act as soon as possible, reducing the chance of an injury worsening.

### 3.2.1.3. Battery Life

The RADIAN system shall operate for a minimum of 3 hours on battery power without recharging.

Rationale: This amount of time will allow the system to stay functioning while the second battery is charging.

### 3.2.1.4. Communication Reliability

The RADIAN system shall send an alert over the Gotify server with a minimum success rate of 95%.

Functional System Requirements | Revision - 2
Rationale: | A reliable communication system will ensure that fall events reach
caregivers promptly, allowing for fast response times.

### 3.2.1.5. Local Alert Functionality

The RADIAN system will be equipped with a local audible alert system that, upon a fall being detected, a minimum of a 70 dB alarm will be activated.

Rationale: Having the local alert system will provide an alert to the user and nearby individuals that a fall has occurred. This will also allow for locating the victim quickly.

### 3.2.1.6. Autonomous Operation

The RADIAN system will operate autonomously, allowing users to have minimal interaction with the device.

Rationale: Autonomy ensures there will be continuous monitoring and timely alerts without the user needing to worry about maintaining the device.

### 3.2.2. Physical Characteristics

### 3.2.2.1. Radar Scan Area

The RADIAN system will operate in a standard room of 20 to 30 square meters with an angle of 45 degrees facing down.

Rationale: The RADIAN system is intended to operate in any standard household
room, including but not limited to dining rooms, living rooms, and bedrooms. However,
the RADIAN system is not rated for the bathroom.

### 3.2.2.2. Mass

The mass of the RADIAN System shall be less than or equal to 0.8 kilograms.

Rationale: A lighter system will be able to be mounted on walls without requiring heavy-duty hardware and support.

### 3.2.2.3. Volume Envelope

The volume envelope of the RADIAN System shall be less than or equal to 5 inches in height, 8 inches in width, and 14 inches in length.

Rationale: A compact system will be able to be mounted on walls, ceiling, or furniture, allowing for portability & relocation.

### 3.2.2.4. Mounting

The mounting information will be available in the RADIAN group’s ICD as well as their user guide.

Rationale: The RADIAN system must be placed at a certain angle and height to capture the entirety of the room it is placed in.

Functional System Requirements | Revision - 2

### 3.2.2.5. Installation

The instructions for installing the RADIAN system are available for reference in the provided user guide. The installation required by the user will be mounting and battery charging/installation, as the phone application will already be installed and set up.

Rationale: The ease of installation allows the user to mount the RADIAN system and
use it, ensuring that anyone can use the system.

### 3.2.3. Electrical Characteristics

### 3.2.3.1. Inputs

a. The presence or absence of any combination of the input signals in accordance with ICD specifications applied in any sequence shall not damage the RADIAN system, reduce its life expectancy, or cause any malfunction, either when the unit is powered or when it is not.
b. No sequence of commands shall damage the RADIAN System, reduce its life expectancy, or cause any malfunction.

Rationale: By design, it should limit the chance of damage or malfunction by user/technician error.

### 3.2.3.1.1 Power Consumption

The maximum peak power of the system shall not exceed 18 watts.

Rationale: Lower power draw will allow the system to run longer, while a high wattage will shorten the runtime.

### 3.2.3.1.2 Input Voltage Level

The input voltage level for the RADIAN system shall be 5.0V.

Rationale: This is the required voltage for devices used in the RADIAN system

### 3.2.3.2. Outputs

### 3.2.3.2.1 Data Output

The RADIAN system shall include a phone application interface compatible with the data system.

Rationale: The RADIAN system will pass information, specifically if a fall was detected,
to a phone app designed for the caregiver of the high-risk individual.

### 3.2.3.2.2 Diagnostic Output

The RADIAN system may include a diagnostic interface for errors that occur within the system and debugging techniques for the system.

Rationale: This will provide a way for the use of the phone app to locate the error and provide solutions for fixing the error.

Functional System Requirements | Revision - 2

### 3.2.3.2.3 Wireless Communication Output

The RADIAN system shall wirelessly communicate with the phone application to alert if a fall is detected, using the Gotify server.

Rationale: Wireless communication will allow the caregiver to be notified, even if they
are not present in the home to hear the audible alarm.

### 3.2.3.2.4 Cloud Data Storage

The RADIAN system will include a cloud storage option to upload data 4 seconds before the fall, during the fall, and 10 seconds after the fall.

Rationale: Cloud storage allows for first responders to know exactly when a fall occurs
and the extent of the severity of the fall.

### 3.2.3.3. Connectors

The RADIAN System shall follow UL 1977 (2022), Component Connectors for Use in Data, Signal, Control, and Power Applications.

Rationale: Following UL 1977 will ensure that we use safe techniques and correctly
rated connectors
for lower power systems.

### 3.2.3.4. Wiring

The RADIAN System shall follow the guidelines outlined in IPC/WHMA-A-620 Class 1 safety requirements.

Rationale: Class 1 establishes basic workmanship for general, low-voltage products.

### 3.2.4. Environmental Requirements

The RADIAN System shall be designed to withstand and operate in the environments and laboratory tests specified in the following section.

Rationale: The RADIAN system will need to function in an indoor setting similar to the common home, with constant pressure and slight variations in temperature

### 3.2.4.1. Thermal

The RADIAN System will be able to operate in an environment between 50 °F and 80 °F

Rationale: The average temperature of many homes and buildings is between 50 °F
and 80 °F, so the system must accommodate these varying temperatures

Functional System Requirements | Revision - 2

## 4. Support Requirements

### 4.1. Wi-Fi Connection

The RADIAN system requires a Wi-Fi connection to communicate with the Gotify server to send the REST POST notification. The user will provide the Wi-Fi connection to support the wireless connection of the RADIAN system.

Rationale: The system will need a Wi-Fi connection for the Raspberry Pi 3 to communicate with the Gotify cloud server. The Raspberry Pi 3’s Wi-Fi connection can
be changed remotely without having to view the GUI of the device.

### 4.2. Wi-Fi or Cellular Data Connection

The caregiver will be required to have a Wi-Fi or Cellular Data connection to receive the push notification from the RADIAN phone application.

Rationale: This allows the push notification to be communicated wirelessly over any distance.

### 4.3. Battery Maintenance

The user or caregiver must maintain the RADIAN system by occasionally changing the rechargeable batteries. They must also charge the depleted batteries to ensure there is always a backup for the system.

Rationale: Having battery maintenance allows the system to operate without protruding cables and will work if a power outage occurs.

### 4.4. Requirements for Customer

The RADIAN system requires a Wi-Fi connection to post an alert to the Gotify cloud server properly. Due to the system's nature, the caretaker will also need to download the phone application to receive push notifications indicating a fall has occurred. The user will have to provide the Wi-Fi connection, but this should not be an issue, as the majority of homes and buildings have some sort of Wi-Fi connection. The caretaker must have a wireless connection, either Wi-Fi or Cellular Data, to receive the push notifications.

Functional System Requirements | Revision - 2

## Appendix A: Acronyms and Abbreviations

GUI | Graphical User Interface
RADIAN | RADar Intelligent Activity moNitoring

# RADIAN - RADar-based Intelligent Activity moNitoring

# Matthew Blackwell Mitch Hoffman Wyatt Johnson

## INTERFACE CONTROL DOCUMENT

INTERFACE CONTROL DOCUMENT

FOR

## RADIAN

TEAM 60

APPROVED BY:

_____________________________
Matthew Blackwell | Date

_____________________________
Prof. Jang | Date

_____________________________
Roman Venegas | Date

Interface Control Document | Revision - 2

### Change Record

Rev . | Date | Originator | Approvals | Description
1 | 10/04/2025 | Matthew Blackwell | | Draft Release
2 | 12/05/2025 | Wyatt Johnson | | Document formatting and updated Electrical Power System

Interface Control Document | Revision - 2

## Table of Contents

Table of Contents | 3
List of Tables | 5
List of Figures | 6
1. Overview | 7
2. References and Definitions | 8
2.1. References | 8
2.2. Definitions | 8
3. Physical Interface | 9
3.1.Weight | 9
3.2. Dimensions | 9
3.2.1. Dimensions of Data Subsystem | 9
3.2.2. Dimensions of Physical Subsystem | 9
3.2.3. Dimensions of Wireless Subsystem | 9
3.3. Mounting | 9
3.3.1. Height | 9
3.3.2. Angle | 9
3.3.3. Locations | 10
4. Thermal Interface | 11
5. Electrical Interface | 12
5.1. Primary Input Power | 12
5.1.1 Electrical | 12
5.1.2 Connector | 12
5.1.3 Wiring | 12
5.2. Charging Interface | 12
5.2.1 Input | 12
5.2.2 Connectors | 12
5.3. Grounding and ESD | 13
5.3.1 Ground | 13
5.3.2 ESD | 13
5.4. User Control Interface | 13
6. Communications / Device Interface Protocols | 14
6.1. Wi-Fi Communication | 14
6.2. Cellular Data | 14
6.3. Internet Protocols | 14
6.4. UART Serial Interface | 14
7. Mobile Application Interface | 15
7.1 Communication Flow | 15
7.2 User Interface | 15

Interface Control Document | Revision - 2
7.3 Platform Compatibility | 15
7.4 Notification Delivery | 15
7.5 Performance Requirements | 15

Interface Control Document | Revision - 2

## List of Tables

Table 1: Data Subsystem Dimensions | 8
Table 2: Physical Subsystem Dimensions | 8
Table 3: Wireless Subsystem Dimensions | 8

Interface Control Document | Revision - 2

## List of Figures

Figure 1: Electrical Power System | 9

Interface Control Document | Revision - 2

## 1. Overview

This Interface Control Document (ICD) will cover the inputs, outputs, controls, and connections between the Physical, Data, and Wireless subsystems of the RADIAN system. This document will be continuously reviewed and updated as the RADIAN group continues to build, test, and integrate each subsystem. The ICD will include descriptions of each component being used in the system, how they interact with one another, and what data is output from each. The electrical connections and wireless interfaces, and protocols will be described in detail to ensure correct integration for success as described in the Concept of Operations (ConOps).

Interface Control Document | Revision - 2

## 2. References and Definitions

### 2.1. References

IEEE 802.11
IEEE Standard for Information Technology – Telecommunications and Information Exchange between Systems
Jan. 23, 1996

### 2.2. Definitions

3GPP | 3rd Generation Partnership Project
API | Application Programming Interface
A | Ampere
AI | Artificial Intelligence
CPU | Central Processing Unit
ConOps | Concept of Operations
g | Grams
GUI | Graphical User Interface
FSR | Functional System Requirements
HTTP | Hypertext Transfer Protocol
ICD | Interface Control Document
IEEE | Institute of Electrical and Electronics Engineers
ML | Machine Learning
mm | Millimeter
REST | Representational State Transfer

Interface Control Document | Revision - 2

## 3. Physical Interface

### 3.1.Weight

The total weight of the RADIAN system, not including the Android device, will be less than or equal to 0.8 kilograms. This weight requirement enables the system to be properly mounted on the chosen room's wall without requiring heavy-duty hardware and support. Given that each subsystem has only a few components, the weight should not exceed the RADIAN group’s given design.

### 3.2. Dimensions

### 3.2.1. Dimensions of Data Subsystem

Component | Length | Width | Height | Weight
Raspberry Pi 3 | 85.6 mm | 56.5 mm | 17 mm | 41.2 g
Table 1: Data Subsystem Dimensions

### 3.2.2. Dimensions of Physical Subsystem

Component | Length | Width | Height | Weight
6.8Ah Power Board | 135.38 mm | 90.46 mm | <2 mm | <90 g
Radome | 190 mm | 120 mm | 55 mm | <230 g
Table 2: Physical Subsystem Dimensions

### 3.2.3. Dimensions of Wireless Subsystem

Component | Length | Width | Height | Weight
TI AWR6843ISK | 103 mm | 57 mm | 16 mm | 91 g
Table 3: Wireless Subsystem Dimensions

### 3.3. Mounting

### 3.3.1. Height

The RADIAN system will need to be mounted at a minimum of 2 meters off the ground. This allows the system to properly scan the room, have good line-of-sight, and detect if a fall has occurred.

### 3.3.2. Angle

The RADIAN system must be mounted to the wall at a 45-degree angle to allow for the maximum amount of area to be scanned by the radar. Having the system parallel to the

Interface Control Document | Revision - 2

ground may prevent certain areas of the room from being scanned and, therefore, prevent proper detection.

### 3.3.3. Locations

The RADIAN system can be located in any common room of a home or building, including but not limited to living rooms, dining rooms, bedrooms, and kitchens. The RADIAN system is not rated for humidity or water exposure, so it cannot be used in the bathroom.

Interface Control Document | Revision - 2

## 4. Thermal Interface

With the Raspberry Pi 3 and TI AWR6843 chip being enclosed in a 3D printed structure, the added thermal heat could cause reliability issues as the RADIAN system runs. Because the system runs continuously, this further increases the chance for potential failures due to overheating. To mitigate these risks, a small heatsink will be added to the Raspberry Pi 3 to ensure that it remains cool as it handles the data and accurately predicts if a fall occurred. A small 30 mm fan will also be installed to provide airflow across both the Raspberry Pi 3 and the AWR6843 chip. These solutions will allow the RADIAN system to run reliably and efficiently.

Interface Control Document | Revision - 2

## 5. Electrical Interface

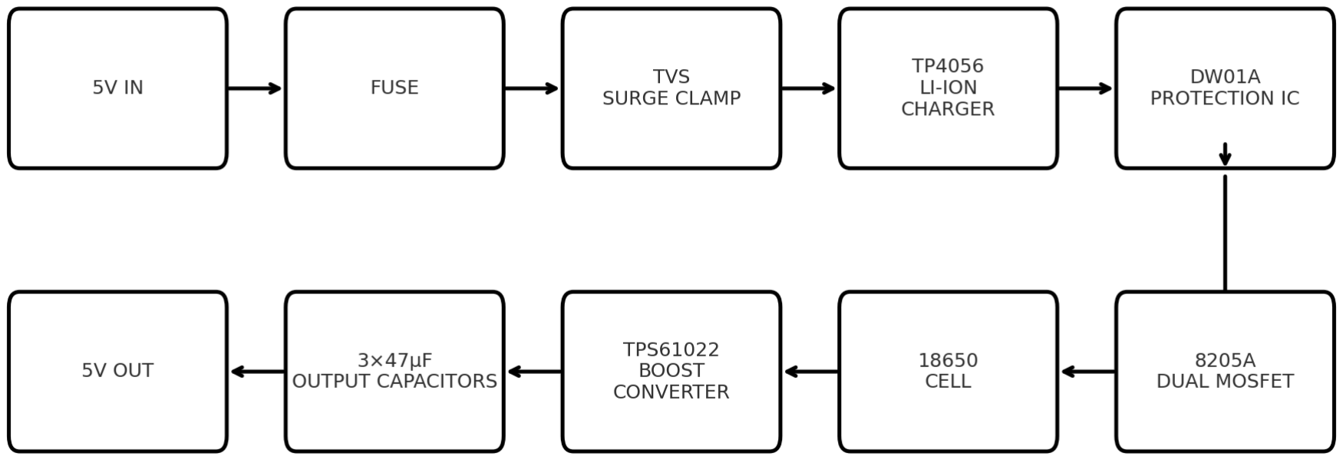
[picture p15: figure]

Figure 1: Electrical Power System

### 5.1. Primary Input Power

### 5.1.1 Electrical

The primary input power of the system will be two 18650 Li-ion cells in parallel, 3.7 V nominal each, for a 7 Ah total capacity. The battery voltage will be stepped up to 5V using a boost converter with a maximum continuous current of 2-3 A.

### 5.1.2 Connector

4-pin locking connector with two positive terminals and two negative terminals for the Raspberry Pi 3 and TI AWR6843.
Pinout (example): 1 = BAT+, 2 = BAT+, 3 = GND, 4 = GND.

### 5.1.3 Wiring

18–20 AWG wiring between the power board and the Raspberry Pi 3/ TI AWR6843. (Target ≤2% drop on the 5 V rail.)

### 5.2. Charging Interface

### 5.2.1 Input

The battery system will be charged using a 5V, 1A wall adapter barrel jack. Charging at a low current will keep the batteries from overheating and ensure safety.

### 5.2.2 Connectors

The battery system will receive its power through a 5V barrel jack connected to a wall adapter.

Interface Control Document | Revision - 2

### 5.3. Grounding and ESD

### 5.3.1 Ground

Single ground plane located on the power PCB.

### 5.3.2 ESD

TVS diodes on the barrel jack and on external connectors.

### 5.4. User Control Interface

The RADIAN system will come with a custom-designed phone application where the caregiver will be able to receive push notifications that a fall has been detected. The app may include a simple battery monitoring system to alert the user when the batteries need to be recharged.

Interface Control Document | Revision - 2

## 6. Communications / Device Interface Protocols

### 6.1. Wi-Fi Communication

The Raspberry Pi 3 will use the IEEE 802.11b/g/n Wi-Fi standards through its onboard communication chip. These standards apply to Wi-Fi 1, Wi-Fi 3, and Wi-Fi 4, each offering new advancements in performance.

### 6.2. Cellular Data

The Gotify server will communicate with the phone application by 5G cellular data, given by the 3GPP standards for 5G wireless communication.

### 6.3. Internet Protocols

The Raspberry Pi 3 will post the alert message through the standard HTTP REST API protocol, allowing the message to be communicated from the Raspberry Pi 3 to the Gotify server.

### 6.4. UART Serial Interface

A UART serial interface will connect the Raspberry Pi 3 to the TI AWR6843ISK. Data shall be exchanged using packets containing radar object data. The Raspberry Pi shall use these packets and convert the radar output into the AI algorithm, which is then sent to the Gotify server.

Interface Control Document | Revision - 2

## 7. Mobile Application Interface

### 7.1 Communication Flow

The Raspberry Pi 3 shall send event data to the Gotify server using an HTTP POST request. The Gotify server will then relay the data to the mobile app via WebSocket connection to receive messages in real time.

### 7.2 User Interface

The app shall display incoming alerts and system messages, battery life, and previous alerts, if any, in a custom-designed user interface.

### 7.3 Platform Compatibility

The app will be developed using Flutter for the user interface and Dart for the programming language. This gives the ability for the app to be run on Android devices.

### 7.4 Notification Delivery

The app shall generate a push notification when it has received an alert message from the Gotify server. The notifications will be displayed using the notification system of the Android device, to ensure the notifications are visible when the app is not open.

### 7.5 Performance Requirements

The alerts shall be delivered to the app within 5 seconds of the Raspberry Pi sending the alert to the Gotify server, under normal network conditions.

# RADIAN - RADar-based Intelligent Activity moNitoring

# Matthew Blackwell Mitch Hoffman Wyatt Johnson

## EXECUTION TIMELINE

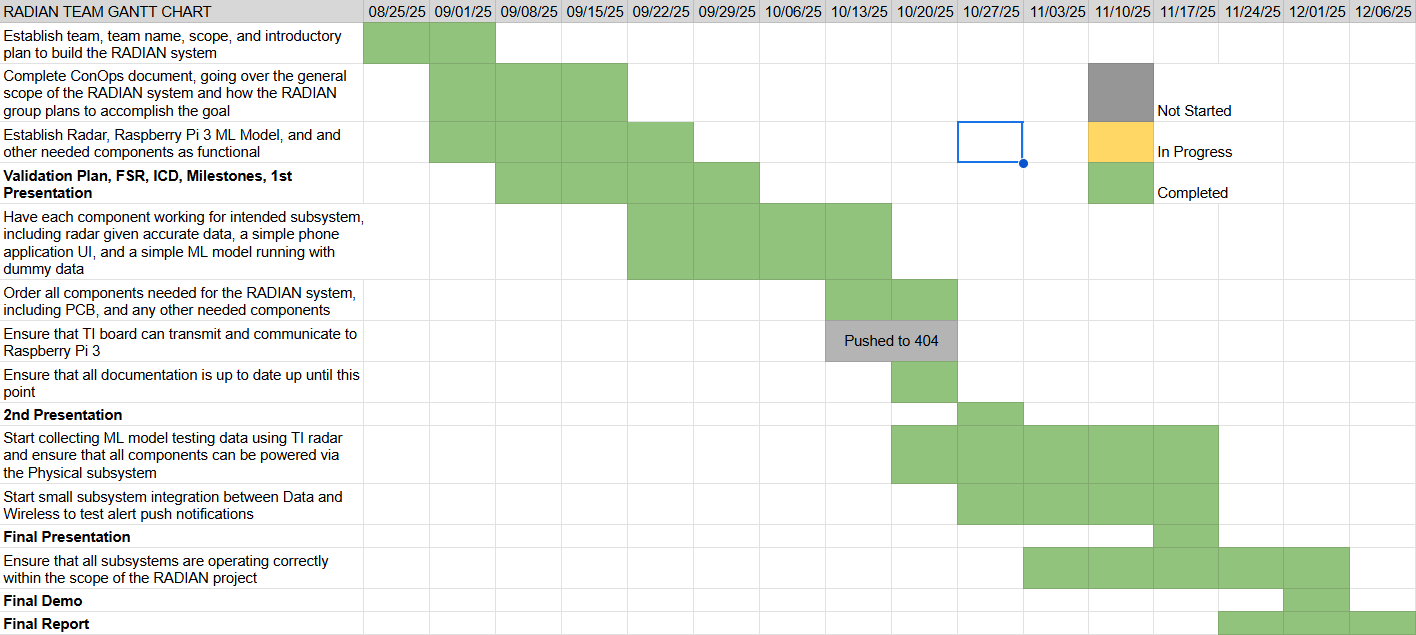
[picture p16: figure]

# RADIAN - RADar-based Intelligent Activity moNitoring

# Matthew Blackwell Mitch Hoffman Wyatt Johnson

## VALIDATION

Power Subsystem
Test | Description | System | Status
WEBENCH Design Simulation | Steady-state, startup, load-transient, and input-transient simulations validate TPS61022 component choices and operating margins | Boost | Completed
ERC/DRC Sign-off | Run schematic/PCB ERC/DRC and waive labeling issue on charger/boost connection | Power Board | Completed
Footprint/BOM Cross-Check | Verify charger, boost, holders, and connector footprints and pin mappings against datasheets | Power Board | Completed
Power Tree Review | Review voltage and current budgets against loads and IC ratings. | Power Board | Completed
Visual & Dimensional Check | Inspect bare PCB size, hole locations, silkscreen, and solder mask vs. the fab drawing | Power Board | Completed
Solderability Check | Test pad finish quality by tinning a coupon/pad and inspecting wetting | Power Board | Completed
Fit Check: 18650 Holders & Connectors | Verify 18650 holders, barrel jack, and connectors seat flat and align with holes before reflow | Power Board | Completed
Reflow Profile Check | Apply paste and reflow; confirm thermal profile is within datasheet limits for ICs | Assembly | Completed
Microscope Inspection | Inspect IC pins and passives for bridges, voids, tombstones, and poor fillets | Assembly | Completed
Polarity/Orientation | Check diodes, LEDs, electrolytics, and IC pin 1 orientation vs. silkscreen | Assembly | Completed
Resistance-to-GND Check | Measure resistance from +BAT and +5 V rails to GND to catch gross shorts before power-on | Power Board | Completed
Limited Bench Power-On | Power VIN from bench supply with current limit; confirm reasonable idle current and no hot spots | Charger/ Boost | Completed

Key Node DC Sanity | Check VIN, battery node, and 5 V rail voltages with no load | Power Board | Completed
Charger Bench Emulation | Emulate battery with bench supply; verify TP4056 charge behavior and status pins vs. datasheet | Charger | Completed
Single-Cell Charge Profile | Charge 18650 cell; log battery voltage over time to confirm CC/CV behavior and termination | Charger | Completed
Dual-Cell Pack Charge Curve | Charge 2 * 18650 batteries; record battery voltage vs. time | Charger | Completed
Charge + Boost Operation | Run TP4056 charging while the boost converter supplies 5 V rail; check for heating or instability | System | Completed
No-Load Output | Measure 5 V rail at no load; verify approximately 5.0 V regulation | Boost | Completed
Startup Under Load | Verify the boost circuit can start up under load | Boost | Completed
Raspberry Pi Load Test | Power Raspberry Pi 3 from the board; verify successful boot and stable ~4.9–5.0 V rail | RADIAN System | Completed
Audible Alarm | Test the decibel of the audible alarm | RADIAN System | Future work

Radar Subsystem
Test | Description | System | Status
UART Communication Integrity Test | Radar correctly transmits binary TLV packets and Python script decodes them | Radar | Completed
Point Cloud Accuracy Test (static target) | Radar accurately reports x, y, z coordinates of stationary object | Radar | Completed
Point Cloud Accuracy Test (moving target/velocity) | Radar accurately reports Doppler-based velocity estimation | Radar | Completed
Multiple Object Detection | Radar can detect more than one target simultaneously | Radar | Completed

Test
Configure File Test (.cfg integration) | Ensure custom configurations change radar behavior | Radar | Completed
Real Time Terminal Display Test | Python file displays live point cloud data without delay or crash | Radar | Completed

App Subsystem
Test | Description | System | Status
App Navigation Test | All tabs function and route correctly | App | Completed
Alert Simulation Test | Fall simulation button triggers critical alert logic | App | Completed
Settings and Server Connection Test | Validate server connection workflow | App | Completed
Gotify Push Notification Test | App receives live notifications from server | App | Completed
Weekly Fall Log Generation Test | Validate automatic weekly log creation | App | Completed
Data Persistence Test | Fall logs persist after app close/restart | App | Completed
UI Responsiveness Test | App layout works on multiple screen sizes | App | Completed

Notification Subsystem

Test | Description | System | Status
Pi-Server Connectivity Test | Verify Raspberry Pi can reach the laptop/host running Gotify via local IP (ping test) | Notification Server | Completed
Gotify Installation | Confirm Gotify server is installed on the Raspberry Pi by inspecting | Notification | Completed

Verification | the pip list and verifying the package | Server
Gotify UI and Token Setup | Test Gotify UI in a web browser via the laptop IP address and create/share the application token for RADIAN | Notification Server | Completed
Basic Message Publishing | Test Python script sending a “Hello World” message via HTTP POST from the Pi to Gotify and verify it appears in the Gotify UI | Notification Server | Completed
Invalid Token Handling | Test server behavior with an incorrect app token and confirm that an error is reported, and the message is not accepted | Notification Server | Completed
Repeated Message Stability | Test repeated message sends in rapid succession from Pi to Gotify and verify no alerts are dropped | Notification Server | Completed
Server Restart Recovery | Restart the Gotify server and confirm it resumes normal operation and can receive new messages | Notification Server | Completed

Artificial Intelligence Subsystem

Test | Description | System | Status
Model Training & Confusion Matrix Check | Verify the random forest classifier correctly separates static vs dynamic motion; inspect accuracy and confusion matrix on synthetic data | Artificial Intelligence | Completed
Synthetic Frame Verification | Run the classifier on known synthetic test frames and verify that predicted labels match the expected labels | Artificial Intelligence | Completed
Edgecase Generation & Inclusion | Generate edge cases (sitting, bending, kneeling, lying down slowly, trip recovery, crawling, pet walking, object drop, hard fall) and include them in training | Artificial Intelligence | Completed
Fall Logic Edgecase Validation | Run the full pipeline (preprocessing, classification, fall detection) on edge cases to verify “No Fall Detected” in non-fall scenarios | Artificial Intelligence | Completed

Normal Fall Scenario Validation | Run the full pipeline on normal fall test cases to verify the system outputs “Fall Detected” when appropriate | Artificial Intelligence | Completed
Demo Accuracy Verification | Confirm that the ML model reaches the current 89% accuracy target during demo conditions, meeting the verification plan | Artificial Intelligence | Completed
Real-Time Performance on Raspberry Pi | Check that point-cloud processing, ML inference, and fall logic run within real-time constraints on the Raspberry Pi without overloading the system | Artificial Intelligence | Completed

# RADIAN - RADar-based Intelligent Activity moNitoring

# Matthew Blackwell Mitch Hoffman Wyatt Johnson

## SUBSYSTEM REPORTS

SUBSYSTEMS REPORT

FOR

## RADIAN

TEAM 60

APPROVED BY:

_____________________________
Matthew Blackwell | Date

_____________________________
Prof. Jang | Date

_____________________________
Roman Venegas | Date

Subsystem Reports | Revision - 1

### Change Record

Rev . | Date | Originator | Approvals | Description
1 | 11/28/2025 | Matthew Blackwell | | Original Release

Subsystem Reports | Revision - 1

## Table of Contents

Table of Contents | 3
List of Tables | 5
List of Figures | 6
1. Introduction | 7
2. Power Subsystem Report | 8
2.1. Subsystem Introduction | 8
2.2. Subsystem Details | 8
2.2.1. Batteries and Storage | 8
2.2.2. Charging | 8
2.2.3. 5 V Conversion and Distribution | 9
2.2.4. Loads and Estimated Current Draw | 9
2.3. Subsystem Validation | 10
2.3.1 Boost Converter Design Simulations | 10
2.3.2 Benchtop Measurements | 12
2.4. Subsystem Conclusion | 13
3. mmWave Radar Subsystem Report | 14
3.1 Subsystem Introduction | 14
3.2 Subsystem Details | 14
3.2.1 Hardware Platform and Radar Configuration | 14
3.2.2 UART Communication Architecture | 14
3.2.3 TLV Frame Parsing and Point Cloud Extraction | 14
3.2.4 Integration With the Data Subsystem | 14
3.3 Subsystem Validation | 15
3.3.1 Functional Testing With Live Radar Data | 15
3.3.2 Configuration File Testing | 15
3.3.3 TLV Parsing Verification | 15
3.3.4 Edge Case Testing | 15
3.4 Subsystem Conclusion | 15
4. Mobile Application Subsystem Report | 16
4.1 Subsystem Introduction | 16
4.2 Subsystem Details | 16
4.2.1 Application Architecture | 16
4.2.2 Gotify Integration and Real Time Alerts | 16
4.2.3 Fall Log Feature and Local Database | 16
4.2.4 Theming and User Interface Experience | 17
4.3 Subsystem Validation | 17
4.3.1 UI and Workflow Testing | 17
4.3.2 Alert Handling and Simulation Testing | 17

Subsystem Reports | Revision - 1
4.3.3 Database Structure Verification | 17
4.3.4 Stability and Performance Testing | 17
4.4 Subsystem Conclusion | 17
5. Notification Server Subsystem Report | 18
5.1 Subsystem Introduction | 18
5.2 Subsystem Details | 18
5.2.1 System Architecture | 18
5.2.2 Server Platform | 18
5.2.3 Raspberry Pi Integration | 18
5.3 Subsystem Validation | 19
5.3.1 Server Deployment and Connectivity Testing | 19
5.3.2 Message Publishing and Payload Validation | 19
5.3.3 Stability and Performance Testing | 19
5.4. Subsystem Conclusion | 19
6. Artificial Intelligence Subsystem Report | 20
6.1 Subsystem Introduction | 20
6.2 Subsystem Details | 20
6.2.1 System Architecture | 20
6.2.2 Machine Learning Model Design | 20
6.2.3 Fall Detection Algorithm | 21
6.2.4 Raspberry Pi Integration | 21
6.3 Subsystem Validation | 21
6.3.1 Model Training and Functional Verification | 21
6.3.2 Edgecase Generation | 22
6.3.3 Frame Classification and Fall Logic Validation | 22
6.3.4 Stability and Performance Testing | 22
6.4. Subsystem Conclusion | 22

Subsystem Reports | Revision - 1

## List of Tables

Table 1: Estimated Current Draw of RADIAN System | 7

Subsystem Reports | Revision - 1

## List of Figures

Figure 1: Functional block diagram of the power subsystem | 8
Figure 2: steady-state output voltage of the TPS61022 at nominal load | 10
Figure 3: TPS61022 Vout vs Time and Vin vs Time | 11
Figure 4: TPS61022 Vout vs Time and Iout vs Time during load transient simulation | 11
Figure 5: TPS61022 Vout vs Time and Iout vs Time during input-voltage transient
simulation | 12
Figure 6: Voltage of batteries vs Time (s) while charging | 13

Subsystem Reports | Revision - 1

## 1. Introduction

The RADIAN system is a radar-based fall-detction device that is designed to autonomously monitor activity in indoor living spaces and then notify caregivers when a high-risk individual person falls. The system collects data via a mmWave radar and uses a machine-learning algorithm to determine if a fall has occurred. After a fall has occurred, the Raspberry Pi will deliver an alert to a mobile application through a notification server. RADIAN is organized into the Power, mmWave Radar, Artificial Intelligence (Data), Notification Server, and Mobile Application subsystems, each with defined roles and interfaces. Every subsystem was validated to meet its requirements. Through this validation, a clear path to full integration into the complete system defined in the ConOps, FSR, and ICD documents will be possible.

Subsystem Reports | Revision - 1

## 2. Power Subsystem Report

### 2.1. Subsystem Introduction

The RADIAN power subsystem is designed to provide a stable 5 V supply to the Raspberry Pi 3 and the TI AWR6843ISK mmWave radar evaluation board. The subsystem will utilize 18650 rechargeable Li-ion batteries that will be recharged via a 5 V barrel jack. This will allow the system to be placed in any location and not depend on wall outlets for power.

The goals of the power subsystem are to deliver a regulated 5 V rail with sufficient current for the Raspberry Pi and radar. Safely charge and protect the Li-ion battery pack. Protect the rest of the system from faults (over-voltage, short circuit, reverse polarity). Provide several hours of runtime from the battery alone.

The power subsystem was tested to confirm its stability, load capability, and basic safety functions. These tests help verify that the subsystem will reliably support the Raspberry Pi and the mmWave radar of the RADIAN system.

### 2.2. Subsystem Details

A simplified block diagram of the subsystem is below.

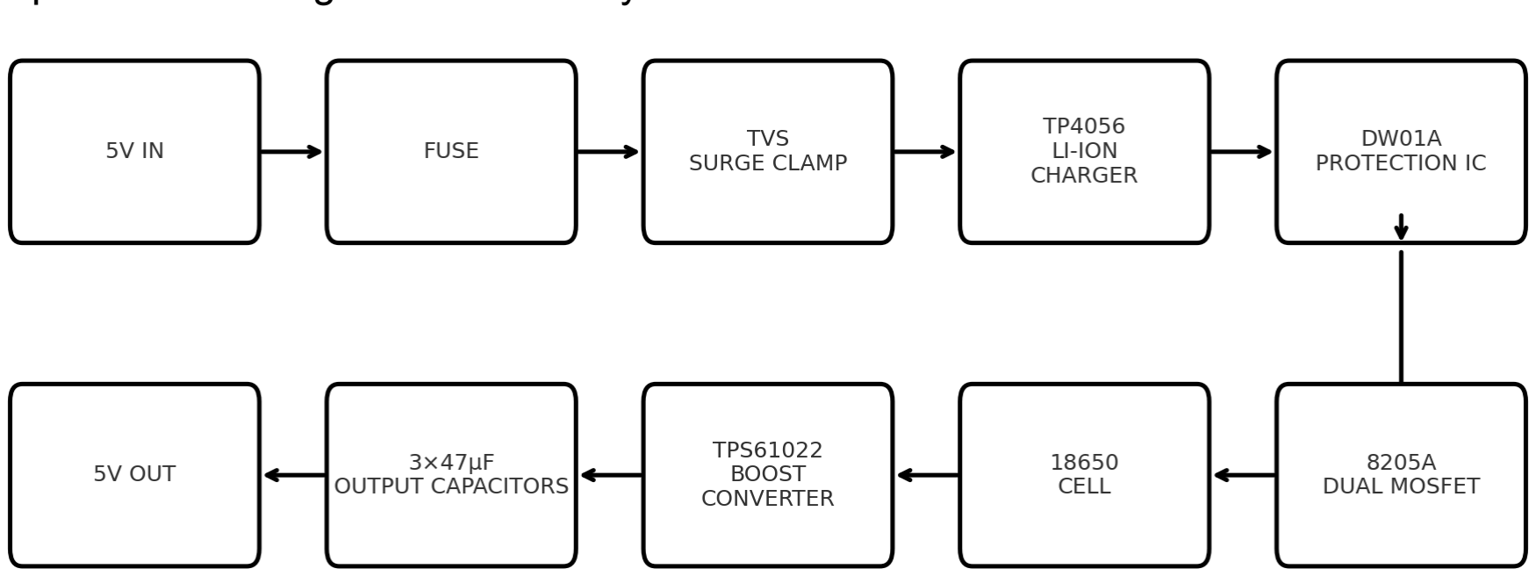
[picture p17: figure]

Figure 1: Functional block diagram of the power subsystem

### 2.2.1. Batteries and Storage

The power subsystem uses two 18650 Li-ion cells (nominal 3.7 V) in parallel to have a total capacity of 6800 mAh. A dedicated protection circuit (DW01A + dual MOSFET pack) provides over-charge, over-discharge, and over-current protection at the cell level. The total stored energy is based on the two 3400 mAh cells in parallel, which provide roughly 25.2 Wh of usable energy at 3.7 V nominal.

### 2.2.2. Charging

A single-cell Li-ion charger IC (TP4056) is used to charge the two batteries from a 5 V barrel jack input. The charger regulates the charge current to a safe level for the cells and will terminate the charge when the battery reaches 4.2V. The design supports up to 2 A input currents. The charger IC will charge the two batteries at a constant current of 1 A.

Subsystem Reports | Revision - 1

Although it is not recommended to charge and use the system due to inefficient charging of batteries, the system can operate while the batteries are charging.

2.2.3. 5 V Conversion and Distribution
A synchronous boost converter (TPS61022) steps the battery voltage from 3.0-4.2V up to a regulated 5 V system rail. The boost converter and board layout are designed for a constant output current of 2-3 A, with short-term peaks above the current limit for inrush or transient loads. For output filtering, there are 3, 47μF ceramic capacitors that help reduce ripple and prevent the 5 V rail from sagging during sudden load increase, such as Raspberry Pi boot or radar startup.

Before finalizing the boost converter design, the TPS61022 circuit was created and analyzed using TI’s WEBENCH design tool. WEBENCH was used to select all the necessary components to allow for a 5V, 2-3 A output from a 3.0-4.2V Li-ion input. The simulations that were run provide an estimated efficiency, output ripple, and component stress, which were used to confirm that the boost design could supply the necessary load currents before building the hardware.

### 2.2.4. Loads and Estimated Current Draw

The primary 5 V loads of the RADIAN system are the Raspberry Pi 3, TI AWR6843ISK mmWave radar evaluation board, and charging status LEDs. The table below shows the approximate current draw for each component.

Component | Voltage | Typical Current Draw | Notes
Raspberry Pi 3 | 5 V | 0.35-0.95 A | 0.35 A idle, up to 0.95 A under 400% CPU load
AWR6843ISK mmWave Radar | 5 V | 0.4-0.8 A (estimated) | Typical current from documentation
Status LEDs | 5 V | <10mA | Calculated based on the series resistor

Table 1: Estimated Current Draw of RADIAN System

Under normal operation of the Raspberry Pi and TI mmWave radar, the total average current is around 1.0-1.8 A, with short peaks on start-up or heavy computations. The boost converter, layout, and connector sizing were selected to comfortably support these loads.

Using the 25.2 Wh battery pack calculation and assuming around 85-90 % efficiency in the boost converter, a continuous 5 V load of roughly 1.5 A (7.5W) corresponds to a runtime of 2.8-3 hours. Actual runtime will vary depending on how heavily the Raspberry Pi and radar are used.

Subsystem Reports | Revision - 1

### 2.3. Subsystem Validation

The RADIAN power subsystem was validated through a series of simulations and benchtop tests to validate the boost converter, charger, and protection circuits, as well as to verify that the system can reliably power the Raspberry Pi and radar.

### 2.3.1 Boost Converter Design Simulations

Prior to building the hardware, the boost converter design was validated using various simulations in TI’s WEBENCH design reports.

### 2.3.1.1 Steady-state analysis

This simulation verified that the TPS61022 was capable of maintaining a regulated 5 V output over the expected input range and load currents while also staying within an acceptable output ripple and inductor/capacitor stress limits.

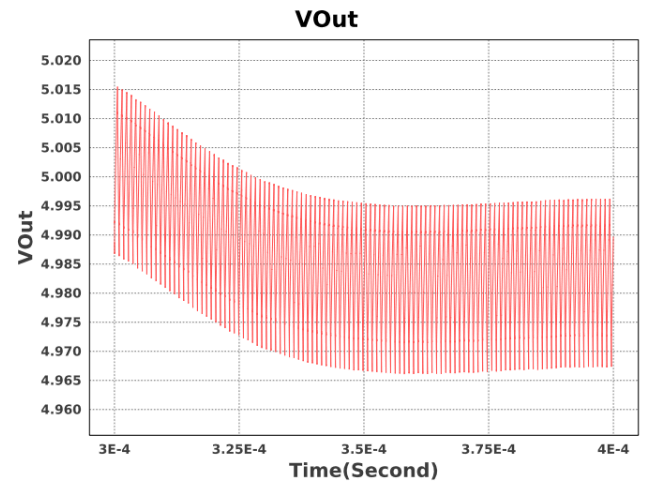
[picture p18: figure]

Figure 2: steady-state output voltage of the TPS61022 at nominal load

Figure 2 shows the 5 V output voltage versus time at nominal load. The x-axis is time (seconds), and the vertical axis is VOUT (volts). The red band represents the output ripple around 5 V. We can see that VOUT remains between 4.8 V and 5.01 V, showing a stable, well-regulated output.

### 2.3.1.2 Startup analysis

This simulation verified that the TPS61022 could start up cleanly under load without having excessive overshoot on the 5 V rail. This will help understand the boost converter capabilities when the Raspberry Pi and TI mmWave radar are connected to the power board.

Subsystem Reports | Revision - 1

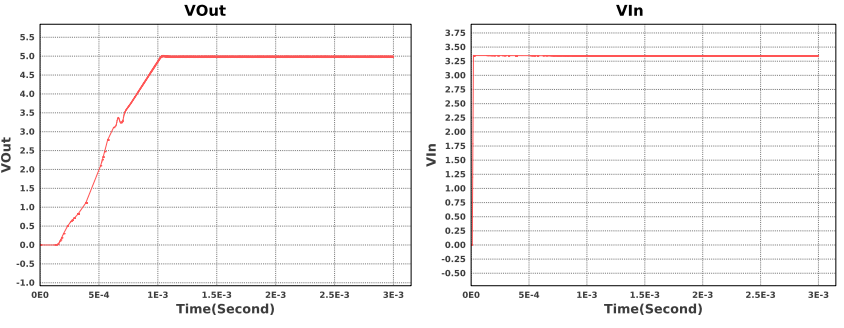
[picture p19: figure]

Figure 3: TPS61022 Vout vs Time and Vin vs Time

Figure 3 shows the simulated startup behavior of the TPS61022. The left graph shows VOUT rising from 0 V to ~5 V in about 1ms with almost no overshoot. The right graph shows VIN remaining nearly constant at about 3.4 V during this time. These figures confirm that the converter starts up quickly and smoothly with little to no voltage spikes on the 5 V rail.

### 2.3.1.3 Load-transient analysis

This simulation verified that the TPS61022 5 V output response to step changes in current, similar to the Raspberry Pi and TI mmWave radar switching between idle and active states.

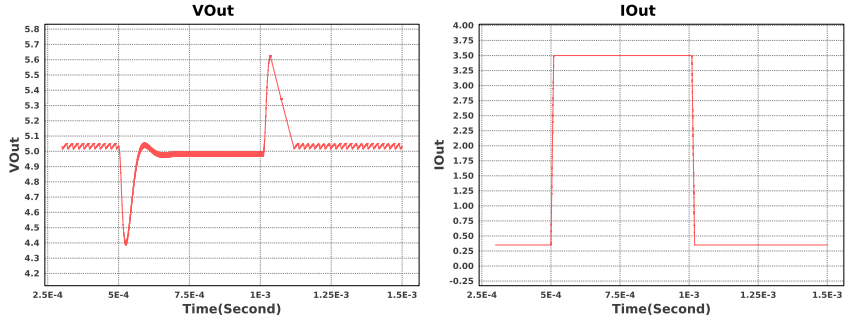
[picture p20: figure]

Figure 4: TPS61022 Vout vs Time and Iout vs Time during load transient simulation

Figure 4 (left graph) shows the simulated 5 V output voltage during a load step, and (right graph) shows the corresponding output current. The load current steps form ~0.3 A to ~3.5 A and then back down to ~0.3A. This step causes a brief overshoot and undershoot on the 5 V rail. In both cases, the output quickly settles back to ~5 V, showing that the converter can handle rapid changes in load without large or long-lasting spikes on the supply.

Subsystem Reports | Revision - 1

### 2.3.1.4 Input-transient analysis

This simulation verified that the TPS61022 could handle the input voltage changing rapidly, emulating the changes in battery voltage, i.e., changing the battery cells.

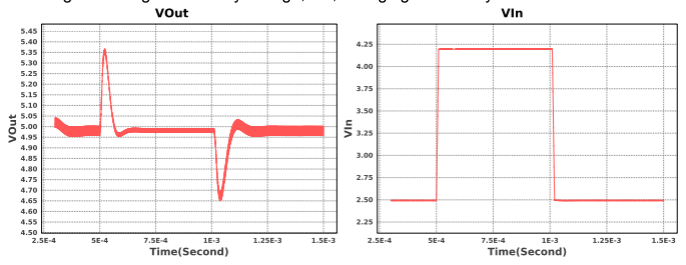
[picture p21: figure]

Figure 5: TPS61022 Vout vs Time and Iout vs Time during input-voltage transient simulation

Figure 5 (left graph) shows the simulated 5 V output voltage, and (right graph) shows the corresponding input voltage. In the simulation results, Vin steps from ~2.5 V to ~4.25 V and then back down to ~2.5V. As Vin changes, Vout shows brief spikes before quickly returning to its steady 5 V output. This shows that the converter maintains regulation on the 5 V rail even when the battery voltage changes suddenly.

### 2.3.2 Benchtop Measurements

After validating the design, the RADIAN power subsystem was assembled and tested. These tests were used to verify that the hardware meets the design goals for output regulation, load capability, and safe battery charging.

### 2.3.2.1 Voltage and Current Testing

The first tests were performed with no load on the output. With no external load connected, the boost converter output measured approximately ~5.03V.

During operation, an unknown amount of current caused a high-current thin trace between the inductor and the TPS61022 switching pin to overheat and open. This is not due to the TPS61022 limitations, but the copper trace design being too thin (5 mil). The failure was noted, and future revisions will increase the trace width to increase current limits. Due to this flaw, load testing was not extensively tested to ensure a fully functional board before the demo.

### 2.3.2.2 Raspberry Pi load test

After completing resistive load testing, the power board was connected directly to a Raspberry Pi 3 to confirm that the subsystem was capable of powering a real digital load. The Pi booted while the 5 V rail was measured using a digital multimeter. During the boot, the measured voltage remained at a constant ~4.92V. This is well within the range that the recommended voltage stays at for the Raspberry Pi.

Subsystem Reports | Revision - 1

### 2.3.2.3 mmWave Radar load test

The TI AWR6843ISK mmWave radar was not directly connected to the power board during testing. Because this board is shared with another member’s subsystem and there was limited time remaining before the final demo, we chose not to risk damaging the radar board.

### 2.3.2.4 Charger and battery behavior

The TP4056 charging circuit was tested by connecting two semi-discharged 18650 batteries in parallel to the board and applying a 5 V input at the barrel jack. The charge-status LED indicators on the TP4056 behaved as expected (red LED on when charging, green LED on when charging is complete). Below are the voltage results of the two batteries recorded over 4 hours and 44 minutes.

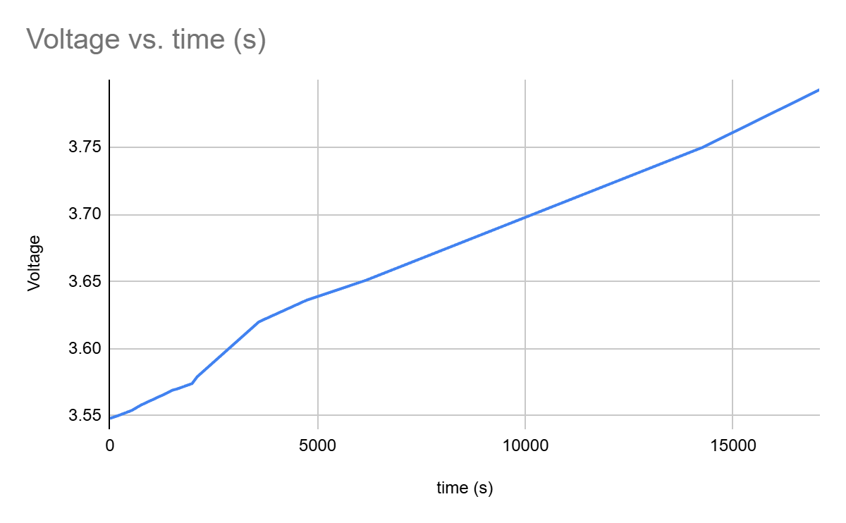
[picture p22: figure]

Figure 6: Voltage of batteries vs Time (s) while charging

Analyzing Figure 6, we can see that the 18650 batteries are reliably charging. While the charge time is long, this is expected since the battery's total capacity is 6.8Ah.

During charging, the boost circuit output was measured at ~5 V while the batteries were charging. Even though this mode is less efficient at charging the batteries and is not recommended for system use, no heating or instability issues were observed during these tests.

### 2.3.2.5 Audible alarm

In the FSR and ConOps, a local audible alarm is planned but not yet implemented. This will be implemented from January to May.

### 2.4. Subsystem Conclusion

Overall, the WEBENCH simulations and physical measurements show that the RADIAN power subsystem meets the core 5 V regulation and Pi load requirements. The boost converter maintains stability across the expected range, the charger safely charges the Li-ion batteries, and the hardware can power a Raspberry Pi 3 reliably. This validated the

Subsystem Reports | Revision - 1

performance of the power subsystem and provided confidence that the RADIAN system will have a reliable and stable power supply, while also providing valuable layout and protection improvements for future revisions.

Subsystem Reports | Revision - 1

## 3. mmWave Radar Subsystem Report

### 3.1 Subsystem Introduction

The mmWave Radar Subsystem is responsible for detecting human presence, monitoring motion, and identifying potential fall events within the RADIAN system. This subsystem uses the Texas Instruments AWR6843ISK radar and a custom Python based UART processing pipeline to extract real time point cloud data. The subsystem serves as the primary sensing module for fall detection and provides the Raspberry Pi Data Subsystem with continuous spatial and velocity information needed for classification algorithms.

### 3.2 Subsystem Details

### 3.2.1 Hardware Platform and Radar Configuration

The subsystem uses the TI AWR6843ISK, a 60-64 GHz FMCW mmWave radar supporting range, Doppler (velocity), and angle estimation. A configuration file (.cfg) generated from TI’s mmWave Visualizer defines the chirp parameters, sampling settings, and processing chains for indoor monitoring. The Python pipeline automatically transmits this configuration to the radar during initialization, ensuring the sensor operates in a mode suitable for fall detection.

### 3.2.2 UART Communication Architecture

The subsystem uses two UART channels, a command line interface UART operating at 115,200 baud for sending configuration commands and a high speed data UART operating at 921,600 baud for receiving binary radar output. The mmwave_run.py script establishes and manages both ports, transmits the full configuration file, and maintains continuous monitoring of incoming radar data. This arrangement enables the radar to receive initialization commands and deliver live measurement data without interruption.

### 3.2.3 TLV Frame Parsing and Point Cloud Extraction

The radar outputs its processed data in a binary TLV (Type-Length-Value) format. The Python pipeline reads these TLVs, identifies the “Detected Points” section, and converts the spherical radar measurements into x, y, and z coordinates, along with velocity values derived from Doppler frequency shifts. The script formats each frame as a separate JSON object using NDJSON formatting, which simplifies integration with downstream software by keeping the data stream clean and machine readable while ensuring debug output remains isolated on STDERR.

### 3.2.4 Integration With the Data Subsystem

The radar subsystem is designed to integrate with the Raspberry Pi Data Subsystem. Although it currently operates independently for testing and development, it will eventually run on the Raspberry Pi, continuously streaming JSON formatted point cloud data to the data processing modules. This real time stream will support AI based fall detection algorithms and enable the collection of presence, motion, and velocity information.

Subsystem Reports | Revision - 1

### 3.3 Subsystem Validation

### 3.3.1 Functional Testing With Live Radar Data

Validation involved operating the radar in indoor environments and confirming that the system correctly identified stationary users, tracked walking motion, and captured rapid movements associated with fall simulations. Real time output in the terminal verified that the TLV frames were being interpreted correctly and that the point cloud data remained stable and continuous.

### 3.3.2 Configuration File Testing

Multiple radar configuration profiles were evaluated to ensure the pipeline operated correctly across different modes. These included short range and medium range indoor profiles. Each configuration produced expected point cloud characteristics, such as consistent frame rates and appropriate numbers of detected points.

### 3.3.3 TLV Parsing Verification

TLV parsing was validated by monitoring the decoded header fields, TLV counts, and detected point quantities produced by the Python script during live testing. The reported packet lengths and number of TLVs consistently matched the expected structure defined by the TI AWR6843ISk data format. In addition, the point cloud output behaved as expected when a person stood or moved at known positions relative to the radar.

### 3.3.4 Edge Case Testing

The subsystem was tested under various conditions, including empty rooms, cluttered environments, multiple moving subjects, and different mounting angles for the radar. In each scenario, the pipeline maintained stable operation and produced valid JSON frames without crashes or distorted output.

### 3.4 Subsystem Conclusion

The mmWave Radar Subsystem successfully demonstrated reliable point cloud data, TLV frame parsing, and UART based communication using the AWR6843ISK platform. Testing confirmed that the radar pipeline consistently produced accurate spatial and velocity data suitable for fall detection algorithms, and the subsystem remained stable across various operating conditions. Although system level integration is still forthcoming, the radar subsystem has been fully developed and validated in isolation, confirming its readiness for incorporation into the complete RADIAN sensing pipeline.

Subsystem Reports | Revision - 1

## 4. Mobile Application Subsystem Report

### 4.1 Subsystem Introduction

The Mobile Application Subsystem provides caregivers an interface for the RADIAN system and plays a central role in delivering fall alerts, presenting system status, and maintaining historical event records. Developed using Flutter for Android devices, the application incorporates a modular, tab based architecture that separates alert handling, historical logging, settings configuration, and system monitoring into distinct, intuitive interfaces. The subsystem is designed to integrate with the RADIAN backend through a Gotify server, enabling real time delivery for fall notifications generated by the mmWave radar subsystem.

### 4.2 Subsystem Details

### 4.2.1 Application Architecture

The mobile application follows a tab based navigation structure that organizes the system’s functionality across four main interfaces, the Home, Alerts, Fall Log, and Settings tabs. The Home tab displays overall system status and highlights active alerts. The Alerts tab allows users to simulate fall events and is designed to display real time alerts received from the Gotify notification server. The Fall Log tab provides caregivers with access to historical fall data and is backed by a local SQLite database implemented though Drift. This database stores fall events in a persistent on device file and supplies the Fall Log interface with structured records for review. The Settings tab enables configuration of the Gotify server endpoint and authentication token, and it also includes theme management options that let users choose between light mode or dark mode for the system’s theme preferences. These components form a modular and scalable application architecture in which the user interface, local storage subsystem, and networked alerting interface are implemented independently but designed for seamless integration.

### 4.2.2 Gotify Integration and Real Time Alerts

The application was designed to receive real time alerts through a Gotify server, which serves as the communication bridge between the Raspberry Pi data subsystem and the mobile device. A custom Dart service manages server configuration, authentication token storage, message parsing, and incoming alert handling. When an alert is received, the app presents a notification and initiates a recurring reminder loop that generates additional notifications every thirty seconds until the alert is acknowledged by the caregiver.

### 4.2.3 Fall Log Feature and Local Database

Persistent event storage is implemented using Drift, which provides a SQLite database stored locally on the device. The database maintains fall event timestamps and event source information. The Fall Log tab queries this database and displays entries chronologically for caregiver review. Although live system alerts were not yet available, the database schema and retrieval methods were validated using simulated entries, ensuring the subsystem is ready for integration.

Subsystem Reports | Revision - 1

### 4.2.4 Theming and User Interface Experience

The application uses Flutter’s Material 3 design system and a custom RADIAN color theme. Users may select light mode or dark mode for the app theme through controls provided in the Settings tab. UI elements were tested on multiple screen sizes to confirm consistent layout, visibility or alerts, and smooth navigation across tabs.

### 4.3 Subsystem Validation

### 4.3.1 UI and Workflow Testing

The user interface and navigation flow were validated using Android emulators to ensure that each tab behaved as intended. Simulated alerts were used to verify that the Alerts and Home tabs correctly displayed active notifications and that the acknowledgement workflows operated smoothly. Navigation between tabs, theme changes, and general responsiveness were also confirmed.

### 4.3.2 Alert Handling and Simulation Testing

Because there is not a system wide integration, alert validation focused on simulated fall events generated within the application. These simulations confirmed that the app could present fall alerts, highlight them in the UI, and clear them upon acknowledgement. Although real alerts from the backend were not available, the internal alert handling logic functioned correctly under test conditions.

### 4.3.3 Database Structure Verification

The SQLite database implemented though Drift was verified to correct creation and schema structure, but no fall events were populated through the RADIAN pipeline since the app is designed to receive entries from the Gotify server during integration. Instead, database functionality was validated by confirming that the database file was created successfully and that the Fall Log tab could render its UI elements, ensuring readiness for future integration.

### 4.3.4 Stability and Performance Testing

The application’s performance was evaluated under repeated simulated alerts, theme changes, and navigation interactions. The app remained stable throughout testing, with no crashes or unexpected behavior, demonstrating that the subsystem is robust and ready for integration with the radar and data subsystems once backend communication is finalized.

### 4.4 Subsystem Conclusion

The Mobile Application Subsystem provides a functional, stable, and modular interface for caregivers, featuring alert simulation, user-configurable settings, theme controls, and a fully implemented local database designed for future fall event logging. While full integration with the Gotify server and backend pipeline has not yet been completed, the application developed correct UI behavior, stable performance, and readiness to receive and store real alerts once system integration is finalized.

Subsystem Reports | Revision - 1

## 5. Notification Server Subsystem Report

### 5.1 Subsystem Introduction

The Notification Server Subsystem plays a critical role in the mission success of the RADIAN system by providing a link between the Artificial Intelligence subsystem and the Mobile Application subsystem. Utilizing the Gotify server architecture, the Raspberry Pi will be able to communicate with the server by posting fall notifications to the server in real-time, allowing for quick and very accurate detection if a fall has occurred. Once the alert has been posted, the Mobile Application will then receive the notification, allowing the caretaker to act quickly to assist the fallen individual.

### 5.2 Subsystem Details

### 5.2.1 System Architecture

The Notification Server Subsystem serves as an intermediary between both the Data pipeline and the communication between the mmWave radar and the mobile application. Once the ML model has classified each point given by the mmWave radar and then detected a fall using the fall detection logic, an alert will be sent through a Python script on the Raspberry Pi. This Python script directly communicates with the Gotify server through the local IP address of the laptop that the RADIAN team tested on. An app token was also created to allow coordination between the Python script, the Gotify server, and the RADIAN mobile application. This architecture was chosen compared to a direct device-to-device connection to allow for increased reliability, scalability, and the possibility of incorporating multiple devices through the system.

### 5.2.2 Server Platform

The Notification Server Subsystem is built around Gotify, a lightweight, open-sourced notification server specifically designed for self-hosted environments. Gotify was selected due to its simple user interface and implementation, vast support throughout the Raspberry Pi community, and its compatibility with local networks, specifically how it interacts with the local IP address of devices. The backend of Gotify provides high performance while maintaining low memory and CPU overhead, allowing the machine learning to run simultaneously and not interfere with the server operations.

### 5.2.3 Raspberry Pi Integration

The Notification Server directly integrates with the Raspberry Pi, therefore serving as both the radar processing platform and the origin point for fall alerts. A simple, lightweight Python script publishes messages to the Gotify server using the standard HTTP POST requests, the standard for server communication in many servers across the globe. The token-based authentication needed for communication between the Pi and Gotify server eliminates the need for credential exchanges, allowing for the system to be both secure and simple to deploy.

Subsystem Reports | Revision - 1

### 5.3 Subsystem Validation

### 5.3.1 Server Deployment and Connectivity Testing

The deployment and connectivity between the Raspberry Pi and the local computer were tested through a “ping” between the two devices, verifying that both systems were able to communicate with each other through the local IP address of the testing laptop. The Gotify server was also downloaded and validated through inspection when viewing the “Pip List” of downloaded libraries on the Raspberry Pi device itself. The Gotify User Interface was also tested and validated through inspection on the laptop by running the Gotify software and opening the UI on a web browser through the IP address, allowing the RADIAN team to create and share the application token needed for testing.

### 5.3.2 Message Publishing and Payload Validation

The message publishing to the Gotify server through HTTP POST was validated by testing the Python script made by the RADIAN team. A simple message of “Hello World” was sent from the Raspberry Pi to the Gotify server and displayed on the Gotify UI as a message from the Raspberry Pi. An additional validation test was conducted to ensure that the server was able to handle incorrect tokens, where an error message was printed showing that the message was not correctly received.

### 5.3.3 Stability and Performance Testing

The subsystem’s performance was evaluated under repeated communications between the Raspberry Pi and the Gotify server. No alerts were dropped when testing multiple messages in rapid succession, and when the server was restarted, the service was still stable and able to receive messages.

### 5.4. Subsystem Conclusion

Overall, the design and validation of the Notification Server Subsystem demonstrate that it reliably fulfills its role within the broader RADIAN architecture. The Raspberry Pi can quickly and accurately send notifications to the Gotify server, ensuring that the caregiver can receive alerts in real time and assist the fallen individual. The subsystem is now ready for integration with the Mobile Application subsystem to communicate directly with the mobile application, removing the need for an intermediary laptop device.

Subsystem Reports | Revision - 1

## 6. Artificial Intelligence Subsystem Report

### 6.1 Subsystem Introduction

The Artificial Intelligence Subsystem plays a central role within the Data Subsystem by determining whether a fall event has occurred using a lightweight yet robust machine-learning pipeline. A Random Forest classifier, implemented in Python using scikit-learn, is used to distinguish static versus dynamic motion using synthesized radar point-cloud data. The classifier evaluates on multiple realistic features, including additive white Gaussian noise, jitter, and small movement shifts across the x-, y-, and z-axes, ensuring reliability under realistic conditions. A Python algorithm is then utilized to detect if a fall has occurred over the last five frames of the received data, printing a message if either a fall has occurred or not, depending on the various cases that were tested. Because this subsystem directly determines whether a fall is occurring, rigorous testing and cautious tuning are essential to minimize false positives while maintaining high sensitivity to true fall events.

### 6.2 Subsystem Details
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

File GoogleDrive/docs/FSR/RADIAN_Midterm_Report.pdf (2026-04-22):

# RADIAN - RADar-based Intelligent Activity moNitoring

# Matthew Blackwell Mitch Hoffman Wyatt Johnson

## CONCEPT OF OPERATIONS

CONCEPT OF OPERATIONS

FOR

## RADIAN

TEAM <60>

APPROVED BY:

_____________________________
Matthew Blackwell | Date

_____________________________
Prof. Jang | Date

_____________________________
Roman Venegas | Date

Concept of Operations | Revision - 1
RADIAN

### Change Record

Rev . | Date | Originator | Approvals | Description
1 | 9/9/25 | Matthew Blackwell | | Baseline Release
2 | 9/20/25 | Matthew Blackwell | | Microcontroller Switch
3 | 10/4/25 | Matthew Blackwell | | MCU removal, SMS removal, and other edits from ICD
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

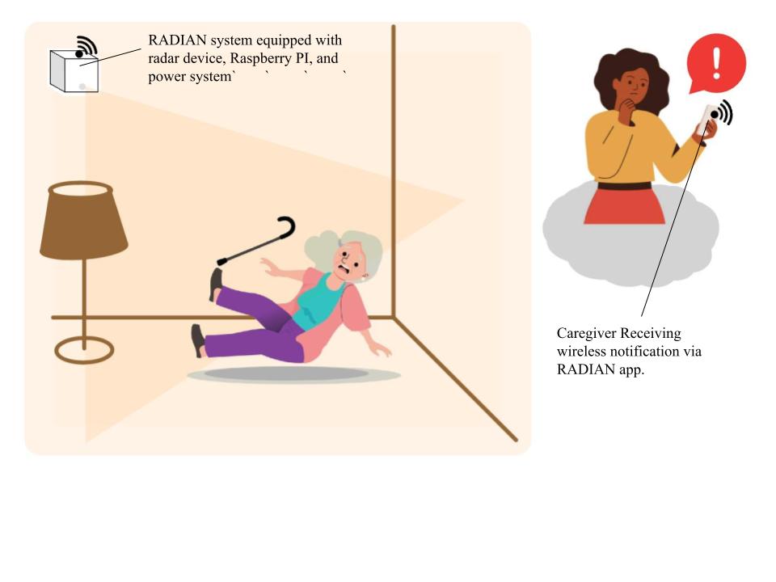
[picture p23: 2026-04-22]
GoogleDrive/docs/FSR/Concept Image.jpg

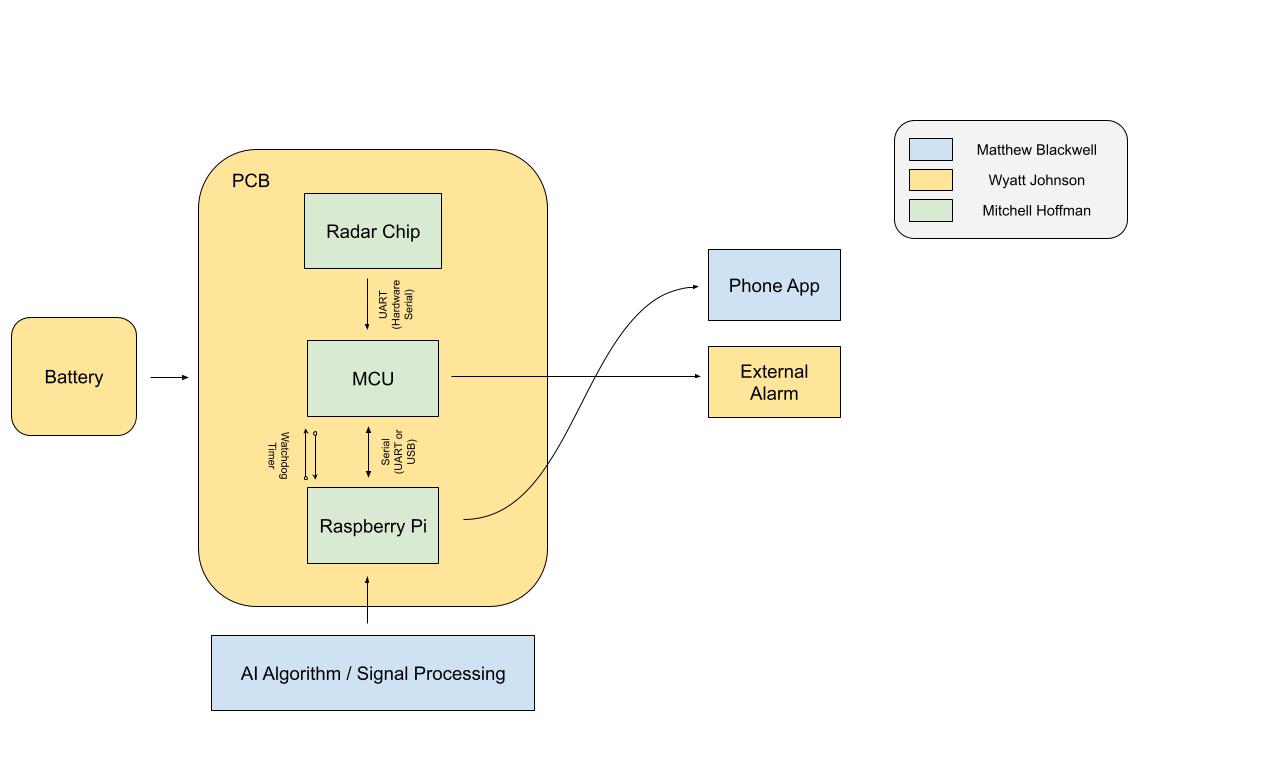
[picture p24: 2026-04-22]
GoogleDrive/docs/ConOps/Extra Documents/RADIAN - High-Level Block Diagram.jpg

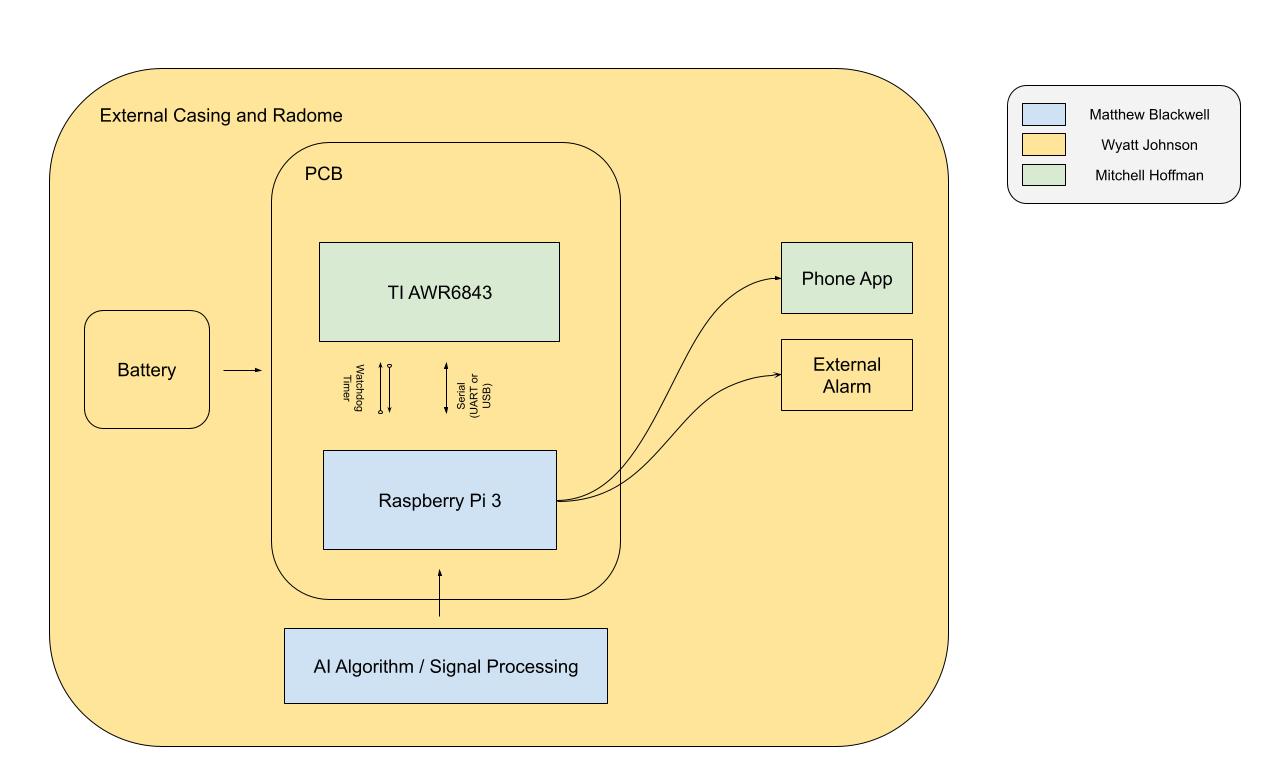
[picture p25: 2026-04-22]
GoogleDrive/docs/ConOps/UPDATED - High-Level Block Diagram.jpg

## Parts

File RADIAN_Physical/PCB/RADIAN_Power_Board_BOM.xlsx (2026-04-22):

Comment | Description | Designator | Footprint | LibRef | Quantity
Component_1 |  |  | NET_TIE | Component_1 | 1
1049 | THM Holder for Dual 18650 Batteries | BT1, BT2 | BAT_1049 | 1049 | 2
0.1uF | SMD Comm X7R, Ceramic, 0.1 uF, 10%, 50 VDC, X7R, SMD, MLCC, Temperature Stable, Class II, 0805 | C1, C2, C4, C8 | CAPC220145_88N_KEM | C0805C104K5RACTU | 4
22uF | Capacitor | C3, C5 | C2220 | C2220C226J3RACTU | 2
1uF | Capacitor | C6, C7 | C0805 | C0805C105J4RAC7210 | 2
10uF | Capacitor | C9 | CAPC3225X280N | UMJ325KB7106KMHP | 1
10nF | Capacitor | C10 | CAPC2012X88N | C0805C103KAREC7210 | 1
22uF | Capacitor | C11, C12, C13 | C1210 | C1210C226K4RACTU | 3
33pF | Capacitor | C14 | CAPC2012X70N | VJ0805A330FXBPW1BC | 1
2.7nF | Capacitor | C15 | C0805 | C0805C272J5GACTU | 1
TVS Diode | Description | CR1 | DO-214AASMB_J-BEND_LTF | SMBJ15A | 1
Diode | Zener Diode 15V 6.1% 500mW SOD123 | Diodes Inc BZT52C15-7-F | D1 | SOD123 | BZT52C15-7-F | 1
FUSE 7A 12V | Description | F1 | FUSE_2920L70012_LTF | 2920L70012MR-A | 1
PACK FUSE 10A | Description | F2 | FUSE_2920L70012_LTF | 2920L70012MR-A | 1
S-8252AAO-M6T1U | Integrated Circuit | IC1 | SOT95P275X135-6N | S-8252AAO-M6T1U | 1
MP2615CGQ-P | Integrated Circuit | IC2 | MP2615CGQP | MP2615CGQ-P | 1
AP64501SP-13 | Integrated Circuit | IC3 | SOIC127P600X163-9N | AP64501SP-13 | 1
Barrel Jack | 2.0 x 6.5 mm, 5.0 A, Horizontal, Through Hole, Tapered Pins, Dc Power Jack Connector | J1 | CUI_PJ-102AH | PJ-102AH | 1
UJC-HP-3-SMT-TR | Connector | J2, J3 | UJCHP3SMTTR | UJC-HP-3-SMT-TR | 2
6.8uH | Inductor | L1 | INDPM6965X300N | IHLP2525CZER6R8M11 | 1
3.6uH | Inductor | L2 | 7447797360 | 7447797360 | 1
GREEN | LED | LED1 | LEDC2012X110N | LTST-C170KGKT | 1
RED | LED | LED2 | LEDC2012X120N | LTST-C170KRKT | 1
PFET IDEAL DIODE | P-CHANNEL 40-V (D-S) MOSFET | Q1 | POWERPAK_SO-8_SINGLE_VIS | SIR4409DP-T1-RE3 | 1
SI7336ADP-T1-GE3 | MOSFET (N-Channel) | Q2, Q3 | SI7141DPT1GE3 | SI7336ADP-T1-GE3 | 2
100k | Description | R1 | RC0805N_YAG | RC0805FR-07100KL | 1
470 | Description | R2, R3 | RC0805N_YAG | RC0805FR-07470RL | 2
2k | No Description Available | R4 | RC0805N_YAG | RT0805FRE072KL | 1
1k | Resistor | R5, R6 | RESC2012X60N | RT0805FRE071KL | 2
25m | Resistor | R7 | RESC6332X71N | WSL2512R0250FEA | 1
10k | Resistor | R8 | RESC2012X60N | RT0805FRE0710KL | 1
115k | Resistor | R10 | RESC2012X60N | AC0805FR-07115KL | 1
15.8k | Resistor | R11 | RESC2012X60N | RC0805FR-0715K8L | 1
100k | Resistor | R12 | RESC2012X60N | CHV0805-FX-1003ELF | 1
22.1k | Description | R13 | RC0805N_YAG | RC0805FR-0722K1L | 1
5.1k | Resistor | R14, R15, R16, R17 | RESC2012X60N | RC0805FR-075K1L | 4
NTC 10k | Thermistor | RT1 | THRMC2012X130N | B57442V5103H062 | 1
EG1218 | Switch | S1 | EG1218 | EG1218 | 1

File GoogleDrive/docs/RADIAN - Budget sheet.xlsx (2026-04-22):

Name | Link | Cost
HiLetgo Charging module | https://www.amazon.com/dp/B00LTQU2RK?psc=1&ref_=cm_sw_r_cp_ud_ct_0FB6R67XCQX70P3W1TGX | $7.79
18650 3500mAh | https://www.18650batterystore.com/checkouts/cn/hWN3aqqXad7GuQCapIj79Ojp/en/information?auto_redirect=false&edge_redirect=true&skip_shop_pay=true | $24.05
PCB Component Order | https://www.digikey.com/short/b9275d2w | $60.26
PCB Order | AdvancedPCB | $99.00
Mirco to Mirco Cable | https://www.amazon.com/gp/product/B01M5GZ3N0/ref=ewc_pr_img_1?smid=A21TE5CLHZDYA7&th=1 | $8.99
Powersystem Cable Assembly | https://www.digikey.com/short/d8744dv8 | $15.69
PCB Component Order | https://www.mouser.com/Tools/SavedCart/Share?AccessID=6ed8b257e1 | $62.06
PCB Component Order | https://www.digikey.com/short/t9b2jwd8 | $13.26
Buzzer | https://www.adafruit.com/wishlists/618373 | 0.98
Wheels | https://www.amazon.com/dp/B0DS8XQYCT?psc=1&ref_=cm_sw_r_cp_ud_ct_G4ZW91X2R7WHNHMN9RSY | 16.99
 |  | $309.07
 | Money left: | $65.93

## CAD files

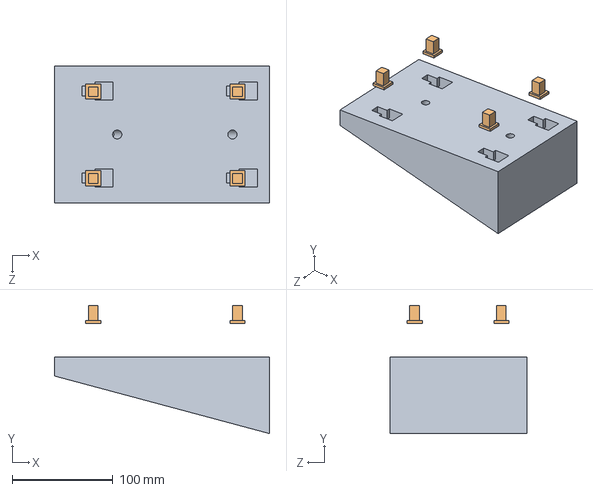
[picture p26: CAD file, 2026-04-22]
RADIAN_Physical/CAD/RADIAN_Enclosure.SLDASM
213.0 x 127.0 x 136.0 mm
Leg x 4
WallMount

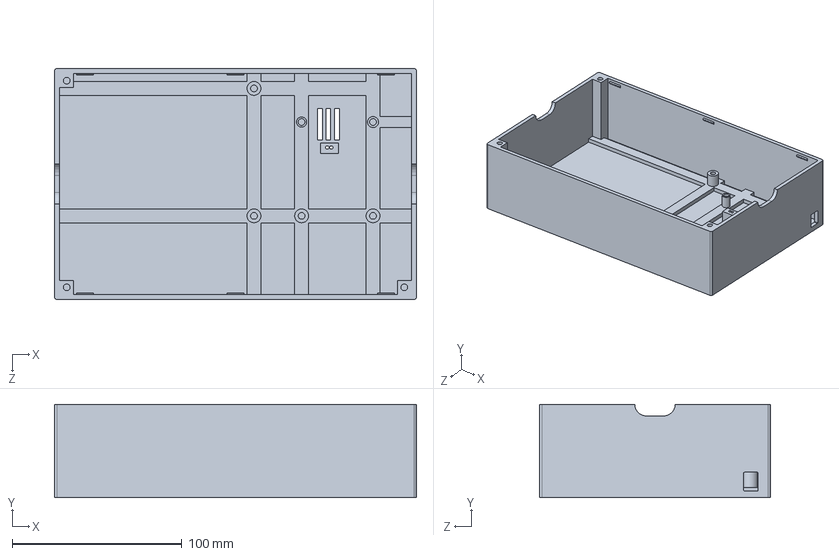
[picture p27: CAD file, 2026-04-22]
RADIAN_Physical/CAD/Enclosure_Bottom.SLDPRT
213.0 x 55.0 x 136.0 mm

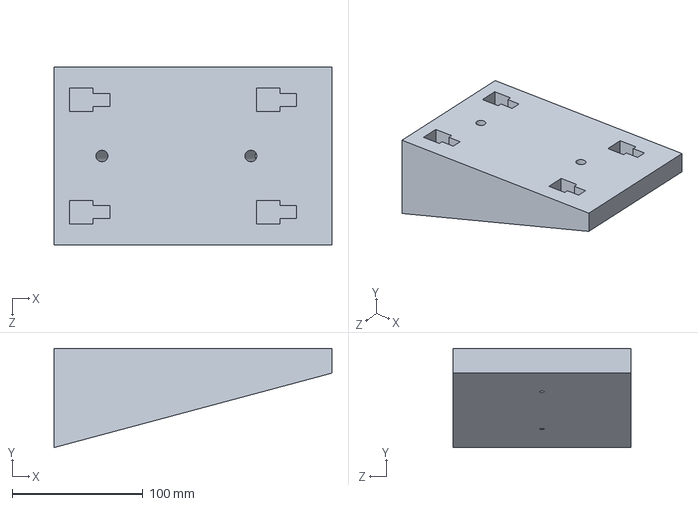
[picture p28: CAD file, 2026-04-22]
RADIAN_Physical/CAD/WallMount.SLDPRT
213.0 x 76.0 x 136.0 mm

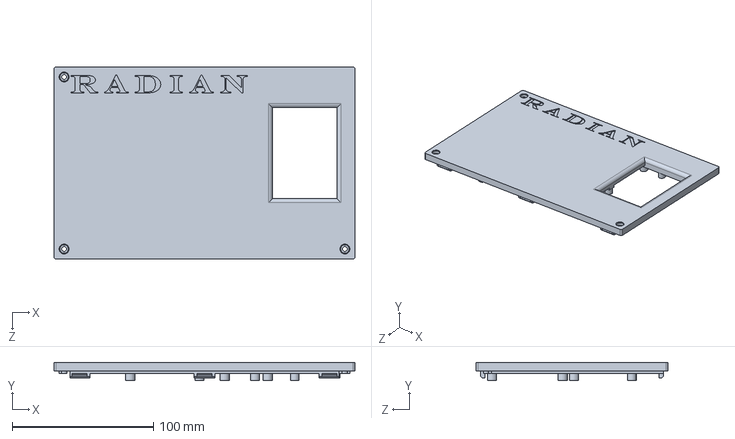
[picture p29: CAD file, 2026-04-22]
RADIAN_Physical/CAD/Enclosure_Lid.SLDPRT
213.0 x 13.0 x 136.0 mm

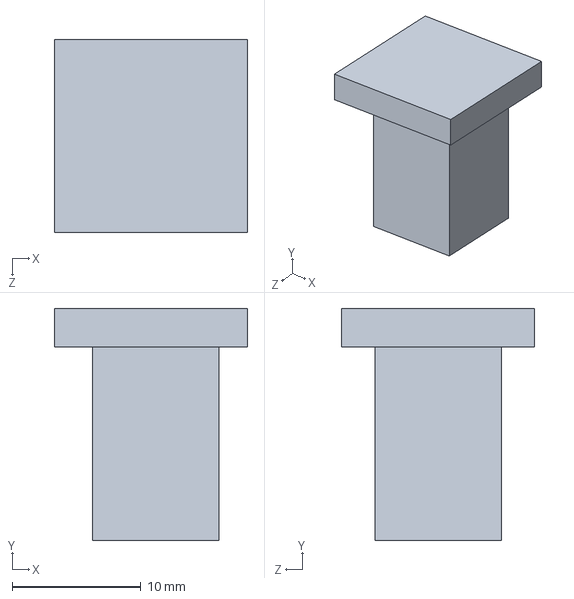
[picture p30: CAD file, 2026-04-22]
RADIAN_Physical/CAD/Leg.SLDPRT
15.0 x 18.0 x 15.0 mm

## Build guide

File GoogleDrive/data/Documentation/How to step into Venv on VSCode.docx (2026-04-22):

cd "C:\Users\matth\OneDrive\Desktop\RADIAN\Decision _Tree_Code"

>> Set-ExecutionPolicy -Scope Process -ExecutionPolicy Bypass

>> .\venv\Scripts\activate

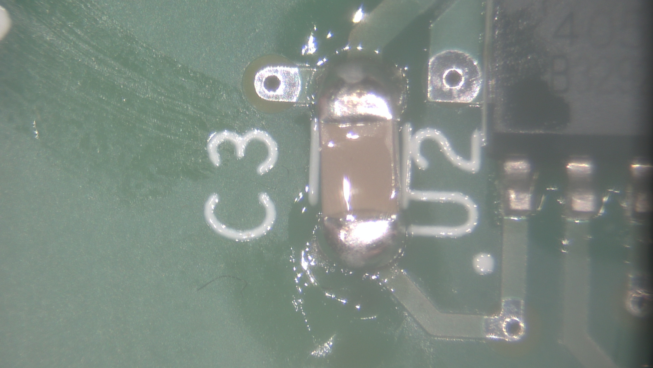
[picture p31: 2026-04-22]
GoogleDrive/physical/power_system/Solder Inspection/IMG00008.JPG

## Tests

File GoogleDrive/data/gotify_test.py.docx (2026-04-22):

import requests

## Configuring these

GOTIFY_URL = "http://10.249.52.19"

APP_TOKEN = "AJTcm8GhyGQKvos"

## Message Details

title = "Pi Notification"

message = "This is a test of Gotify server. Going from the Raspbery Pi to a computer connected to the server. This test occured on Tuesday, October 21st at 9:57am"

priority = 5

## Send to Gotify (Use this to test) --------------

payload = {

"title": "Test Notification",

"message": message,

"priority": 5

}

response = requests.post(

f"{GOTIFY_URL}/message?token={APP_TOKEN}",

json = payload,

headers = {"Content-Type" : "application/json"}\

)

print(response.status_code, response.text)

#def notify(title, message, priority = 5):

# try:

# response = requests.post(

# f"{GOTIFY_URL}/message?token={APP_TOKEN}",

# json = {"title": title, "message": message, "priority": priority},

# timeout = 5

# )

# response.raise_for_status()

# print("Notification sent!")

# except Exception as e:

# print("Notification failed: {e}")

# How it is used:

#from gotify_notify import notify

#notify("Radar Test Complete", "All scanes finished successfully.")

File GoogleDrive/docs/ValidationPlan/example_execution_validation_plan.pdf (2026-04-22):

# Integration/Execution Timeline

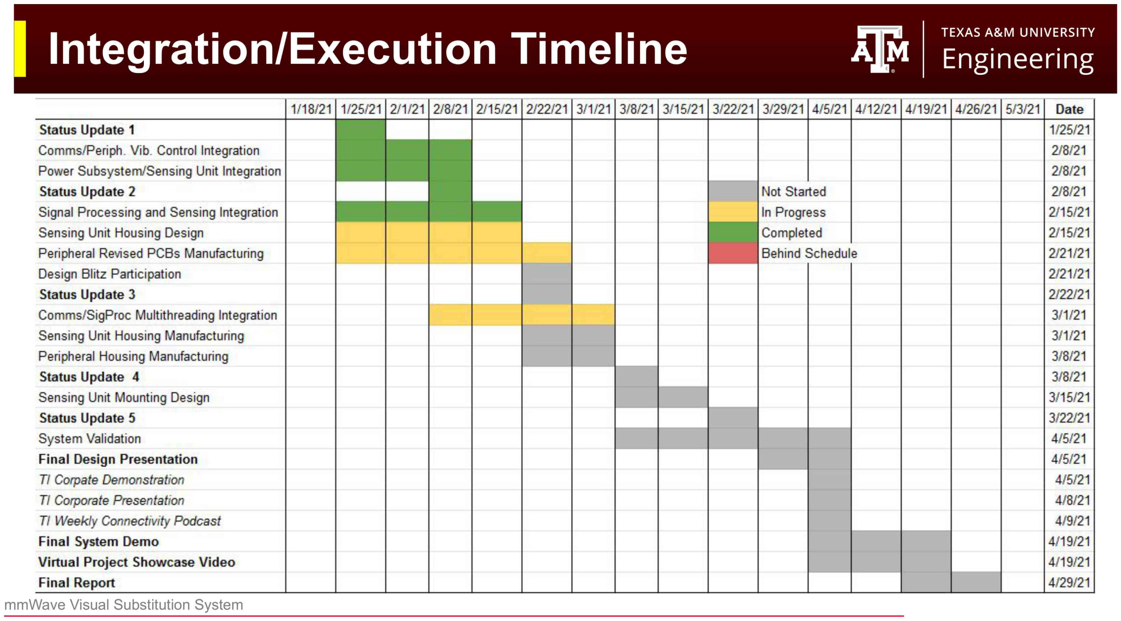
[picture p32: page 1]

# Validation Plan

Paragraph #Test Name | Success Criteria | Methodology | Status

Responsible
Engineer(s)
3.2.1.1 | Communication Range | Sensing unit and peripherals communicate object data and peripheral status when seperated at all ranges up to 7ft | Peripheral self-test and object reporting functions are performed at 1ft intervals ranging from Oft to
| | | 10ft.

### Evan Ross

### UNTESTED Kyle Patrick

3.2.1.2 | System Latency | Haptic feedback is triggered no greater than 0.5s after object enters detection range | Object is placed within system FOV. A stopwatch is used to time the delay between the object
| | | entering the system FOV and haptic feedback on the peripherals. | UNTESTEDFull Team

3.2.1.3

| Wireless Connection
| Stability | Sensing unit and peripherals connection does not drop more than 1 time per 5 minutes and shall reconnect within 10s | 30min. Connection stability is monitored via UART connection on peripherals. | UNTESTED Evan Ross

### 3.2.1.4 Operation Time

| | | System is put into default operational state (5ft peripheral/sensing unit sep.) and left to run for
| | | 60min.Power is monitored via UART connection with peripherals. | UNTESTED Evan Ross
3.2.1.5 | Field of View (FOV) | System detects objects with 60 degrees radially w.r.t direction user is facing. | Measure the system's response to objects that willbe placed inside and outside of the target
| | | field of view | UNTESTED Wil Pinon
3.2.1.6 | Detection Range | System detects objects 6ft radially from device with specified FOV. | Measure the system's response to objects that will be placed inside and outside of the target
| | | range | UNTESTED Will Pinon
3.2.1.7 | Detection Accuracy | System reports false detection less than 5% of operation time | Place objects in detection range across 30min duration. Monitor detected objects over UART on
| | | sensing unit.Compare results. | UNTESTED

Will Pinon

## Evan Ross

Will Pinon
3.2.1.8 | Detection Sensitivity | Objects with angular resolutions as small as 2deg are detected. | Calculate resolution of object and determine if it is detected | UNTESTEDEvan Ross
Kyle Patrick,
3.2.1.9 | Ease of Use | Sysem is attached to the user, by the user, in less than 3 minutes. | Use stopwatch while user is putting on device | UNTESTED Evan Ross
Kevin
3.2.2.1 | Mass | Mass of the sensor and signal processing unit shall not exceed 1lb
The sensor and signal processing unit of the system shall be contained in an enclosure with an envelope of no more than Perform area measurements on the enclosures created for the sensing unit and the peripheral
| | | | UNTESTEDKronenberger
3.2.2.2 | Volume Envelope | 100 cubic inches.The volume envelope of a single peripheral will not exceed 2.5 cubic inches | devices | UNTESTEDFull Team

### 3.2.2.3 Mounting

| | The sensing unit is able to be mounted to the user's head or torso. The peripheral units are able to be mountable to the
| | user's arms and legs. | Calculate the center of mass of the sensing system and determine if objects can be mounted on
| | | user | UNTESTEDFull Team
| | The input voltage level for the TI mmWAVEICBOOsT board shall be 5V and the input voltage level for the TI CC2652 | | Kevin
3.2.3.1.1
3.2.3.1.2

Input Voltage (Sensing UnitLaunchpad device shall also be 5V

| | The input voltage level for the peripheral devices shall be 2.7V-4.3V.The power consumption shall not exceed 0.5W. | Use multimeter to validate input voltage levels | UNTESTEDKronenberger
| Input Voltage (Peripherals) | | Use multimeter to validate input voltage levels | UNTESTED Kyle Patrick

3.2.3.1.3

Peripheral Battery Charging
| Voltage and Current | | Use multimeter and oscilloscope to validate voltage levels and charge current levels | UNTESTEDKyle Patrick
3.2.4.1 | Thermal Resistance | The system should be able to operate in evinronments with temperatures raning from 0C to 45C | Use heating device (oven?) to raise temperature to 45C and then test system functionality.Place
| | | system inside of freezer set to 0C and test it once it has soaked there | UNTESTEDEvan Ross
N/A | Full System Demo | A user of the system is able to navigate an obstacle course and an environemnt they are unfamiliar with. | Team member wears the full system and an obstacle couse is created that they must pass
| | | through.This person could also be lead outside and told to navigate a certain distance. | UNTESTEDFull Team

# mmWave Visual Substitution System

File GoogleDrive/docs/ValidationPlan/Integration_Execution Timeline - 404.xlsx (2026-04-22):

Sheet: TEAM
RADIAN TEAM GANTT CHART | 2026-01-26 | 2026-02-02 | 2026-02-09 | 2026-02-16 | 2026-02-23 | 2026-03-02 | 2026-03-09 | 2026-03-16 | 2026-03-23 | 2026-03-30 | 2026-04-06 | 2026-04-13 | 2026-04-20 | 2026-04-27
Reacquaint team, review documentation, review subsystem work, and plan for the rest of 404
Order any final parts for subsystems |  |  |  |  |  |  |  |  |  |  | Not Started
Confirm that subystem is ready to integrate, if not, review and refine subsystem |  |  |  |  |  |  |  |  |  |  | In Progress
Bi-Weekly Presentation 1 |  |  |  |  |  |  |  |  |  |  | Completed
Integrate with Data and Wireless by confirming communication from Raspberry Pi to phone app
Have all changes finished and updated for individual subsytems
Bi-Weekly Presentation 2
Integrate Physical with Data & Wireless by powering both Rasp. Pi and radar board independently of a power supply
Integrate Data and Wireless to allow basic communication between two devices
Design Blitz
Test previous integration
Bi-Weekly Presentation 3
Have all parts ordered and made for integration
Integrate Physical with Data & Wireless by placing all components into housing
Start falling and edgecase trials with Data and Radar, ensuring many trials of each case
Integrate Data with Wireless by communicating live data from radar to ML model
Test previous integration
Bi-Weekly Presentation 4
Ensure all documentation is up to date
Start full system testing in accordance and in conjuction with Validation Plan
Bi-Weekly Presentation 5
Continue any debugging from full system testing
Retrain & improve fall detection accuracy to meet 90% requirement
Complete remaining validation tasks (Battery Life, Power Consumption, Autonomous Boot)
Final Presentation
Final Demonstrations
Engineering Project Showcase
Final Report
FOR UPDATE PRESENTATION #2
RADIAN TEAM GANTT CHART | 2026-02-16 | 2026-02-23
Have all changes finished and updated for individual subsytems
Start falling and edgecase trials with Data and Radar, ensuring many trials of each case
Bi-Weekly Presentation 2
Integrate with Data and Wireless by confirming communication from Raspberry Pi to phone app
Test previous integration
Design Blitz
Integrate Physical with Data & Wireless by powering both Rasp. Pi and radar board independently of a power supply
Test previous integration
Have all parts ordered and made for integration
Integrate Data with Wireless by communicating live data from radar to ML model
Bi-Weekly Presentation 3
FOR UPDATE PRESENTATION 4
RADIAN TEAM GANTT CHART | 2026-03-16 | 2026-03-23 | 2026-03-30 | 2026-04-06 | 2026-04-13
Start falling and edgecase trials with Data and Radar, ensuring many trials of each case
Integrate Data with Wireless by communicating live data from radar to ML model
Test previous integration
Start full system testing in accordance and in conjuction with Validation Plan
Continue any debugging from full system testing in conjuction with Validation Plan
Ensure all documentation is up to date

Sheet: MITCHELL
WIRELESS GANTT CHART | 2026-01-12 | 2026-01-19 | 2026-01-26 | 2026-02-02 | 2026-02-09 | 2026-02-16 | 2026-02-23 | 2026-03-02 | 2026-03-09 | 2026-03-16 | 2026-03-23 | 2026-03-30 | 2026-04-06 | 2026-04-13 | 2026-04-20 | 2026-04-27
Begin to integrate with ML model and train with the radar's data |  |  |  |  |  |  |  |  |  |  |  | Completed
Validating radar data (filtering, tracking, etc.)
Completing falling and non-falling trials to gather data for various test cases

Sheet: MATTHEW
DATA GANTT CHART | 2026-01-12 | 2026-01-19 | 2026-01-26 | 2026-02-02 | 2026-02-09 | 2026-02-16 | 2026-02-23 | 2026-03-02 | 2026-03-09 | 2026-03-16 | 2026-03-23 | 2026-03-30 | 2026-04-06 | 2026-04-13 | 2026-04-20 | 2026-04-27
Review old subsytem and learn if it will be viable for integration
Research updated ML model and learn how it will work differently than previous iteration |  |  |  |  |  |  |  |  |  |  |  |  | Not Started
Start coding new learning model for updated pipline |  |  |  |  |  |  |  |  |  |  |  |  | In Progress
Validate new CNN model with dummy data |  |  |  |  |  |  |  |  |  |  |  |  | Completed
Collect real training data for new CNN ML model using radar
Integrate with Wireless by sending a push notification from Raspberry Pi to moblie app using Gotify server
Test previous integration
Train first ML model and test it with other RADIAN recorded data
Integrate with Phyical by having Raspberry Pi be powered by the battery
Test previous integration
Train second iteration of ML model and test for accuracy
Train third iteration of ML model and test for accuracy
Test live action mode, simulating real working environment with ML model
Integrate with Physical by placing Raspberry Pi in enclosure
Test previous integration
Improve on model depending on previous test
Debug any Data issues regarding full system functionality
FOR UPDATE PRESENTATION 2
DATA GANTT CHART | 2026-02-02 | 2026-02-09 | 2026-02-16 | 2026-02-23
Validate new CNN model with dummy data
Collect real training data for new CNN ML model using radar
Integrate with Wireless by sending a push notification from Raspberry Pi to moblie app using Gotify server
Test previous integration
Train first ML model and test it with other RADIAN recorded data
Integrate with Phyical by having Raspberry Pi be powered by the battery
Test previous integration
FOR UPDATE PRESENTATION 3
DATA GANTT CHART | 2026-02-16 | 2026-02-23 | 2026-03-02 | 2026-03-09
Validate new CNN model with dummy data
Collect real training data for new CNN ML model using radar
Train first ML model and test it with other RADIAN recorded data
Integrate with Phyical by having Raspberry Pi be powered by the battery
Test previous integration
Train second iteration of ML model and test for accuracy
Train third iteration of ML model and test for accuracy
FOR UPDATE PRESENTATION 4
DATA GANTT CHART | 2026-03-16 | 2026-03-23 | 2026-03-30 | 2026-04-06
Fix errors in integration from Wireless to Data (Pipeline from Radar to Raspberry Pi)
Collect real training data for new CNN ML model using radar
Train second iteration of ML model and test for accuracy
Train third iteration of ML model and test for accuracy
Integrate with Physical by placing Raspberry Pi in enclosure
Test previous integration
Test live action mode, simulating real working environment with ML model
Improve on model depending on previous test
Debug any Data issues regarding full system functionality

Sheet: WYATT
PHYSICAL GANTT CHART | 2026-01-12 | 2026-01-19 | 2026-01-26 | 2026-02-02 | 2026-02-09 | 2026-02-16 | 2026-02-23 | 2026-03-02 | 2026-03-09 | 2026-03-16 | 2026-03-23 | 2026-03-30 | 2026-04-06 | 2026-04-13 | 2026-04-20 | 2026-04-27
Validate radar performace in final setup
Runtime / power verification in assembled system
Fix any issues found during testing
Polish appearance of design
Capture final data, plots, and photos
Prepare final documentation

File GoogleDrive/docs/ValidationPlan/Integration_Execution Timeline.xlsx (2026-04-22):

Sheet: TEAM
RADIAN TEAM GANTT CHART | 2025-08-25 | 2025-09-01 | 2025-09-08 | 2025-09-15 | 2025-09-22 | 2025-09-29 | 2025-10-06 | 2025-10-13 | 2025-10-20 | 2025-10-27 | 2025-11-03 | 2025-11-10 | 2025-11-17 | 2025-11-24 | 2025-12-01 | 2025-12-06
Establish team, team name, scope, and introductory plan to build the RADIAN system
Complete ConOps document, going over the general scope of the RADIAN system and how the RADIAN group plans to accomplish the goal |  |  |  |  |  |  |  |  |  |  |  |  | Not Started
Establish Radar, Raspberry Pi 3 ML Model, and and other needed components as functional |  |  |  |  |  |  |  |  |  |  |  |  | In Progress
Validation Plan, FSR, ICD, Milestones, 1st Presentation |  |  |  |  |  |  |  |  |  |  |  |  | Completed
Have each component working for intended subsystem, including radar given accurate data, a simple phone application UI, and a simple ML model running with dummy data
Order all components needed for the RADIAN system, including PCB, and any other needed components
Ensure that TI board can transmit and communicate to Raspberry Pi 3 |  |  |  |  |  |  |  | Pushed to 404
Ensure that all documentation is up to date up until this point |  |  |  |  |  |  |  |  |  |  |  |  |  |  |  |  | `
2nd Presentation
Start collecting ML model testing data using TI radar and ensure that all components can be powered via the Physical subsystem
Start small subsystem integration between Data and Wireless to test alert push notifications
Final Presentation
Ensure that all subsystems are operating correctly within the scope of the RADIAN project
Final Demo
Final Report

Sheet: MITCHELL
 | 2025-08-25 | 2025-09-01 | 2025-09-08 | 2025-09-15 | 2025-09-22 | 2025-09-29 | 2025-10-06 | 2025-10-13 | 2025-10-20 | 2025-10-27 | 2025-11-03 | 2025-11-10 | 2025-11-17 | 2025-11-24 | 2025-12-01
Research on subsystem
Trade studies on component selection
Select radar and run demo of radar |  |  |  |  |  |  |  |  |  |  |  |  | Not Started
Select and install software for radar data processing |  |  |  |  |  |  |  |  |  |  |  |  | In Progress
Install software for mobile app development |  |  |  |  |  |  |  |  |  |  |  |  | Completed
Radar bring-up and data link setup |  |  |  |  |  |  |  |  |  |  |  |  | Behind Schedule
Radar to Pi integration
Gotify communication and app framework setup
Mobile app development
End to end testing (radar to pi, gotify to app)
System validation and documentation
Integration and Demo prep

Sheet: MATTHEW
 | 2025-08-25 | 2025-09-01 | 2025-09-08 | 2025-09-15 | 2025-09-22 | 2025-09-29 | 2025-10-06 | 2025-10-13 | 2025-10-20 | 2025-10-27 | 2025-11-03 | 2025-11-10 | 2025-11-17 | 2025-11-24 | 2025-12-01
Requirements of the Data subsystem |  |  |  |  |  |  |  |  |  |  |  |  | Not Started
Trade studies and component selection |  |  |  |  |  |  |  |  |  |  |  |  | In Progress
Establish correct Raspberry Pi OS on component and establish a RADIAN GitHub |  |  |  |  |  |  |  |  |  |  |  |  | Completed
Research all connectivity between Raspberry Pi 3 and Android phone and select a communication protocol and server to communicate with phone application |  |  |  |  |  |  |  |  |  |  |  |  | Behind Schedule
Create simple decision tree ML model with dummy data, similar to potential parameters that will be used from the radar
Continue to refine decision tree ML model with accurate dummy data and start coding a random forest ML model
Small integration with Wireless to ensure that data can be transmitted from the TI board to the Raspberry Pi 3
Search and select a potential data set to use for an ANN as well as to test the ML models
Start recording fall detection tests with RADIAN radar to train the ML model
Refine all simple ML models and continue to test accuracy of said models
Continue to update documentation as needed when continuing to test the Data subsystem
Start validation testing to establish reliability in the Data subsystem
Complete validation testing for Data subsystem
Small integration with Wireless to ensure that the fall alert can be communicated to the phone application via Gotify's cloud servers
Review all final documentation and make any needed edits
Final adjustments and demo of Data subsystem

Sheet: WYATT
WYATT'S GANTT CHART
 | 2025-08-25 | 2025-09-01 | 2025-09-08 | 2025-09-15 | 2025-09-22 | 2025-09-29 | 2025-10-06 | 2025-10-13 | 2025-10-20 | 2025-10-27 | 2025-11-03 | 2025-11-10 | 2025-11-17 | 2025-11-24 | 2025-12-01
Research Power Requirements & Li-ion Cell Types: confirm loads, runtime, and safe cell options.
Requirements & Specs: Limits and pass/fail criteria. |  |  |  |  |  |  |  |  |  |  |  |  | Not Started
Battery Selection: choose cells/pack that meet the 4+ hr goal. |  |  |  |  |  |  |  |  |  |  |  |  | In Progress
Charger IC Selection & Setup: pick the charger and default limits. |  |  |  |  |  |  |  |  |  |  |  |  | Completed
Power Electronics Design (Schematic & PCB): capture, lay out, and label the power board. |  |  |  |  |  |  |  |  |  |  |  |  | Behind Schedule
Prototype Assembly: build Rev A and sanity-check power.
PCB validation: Have PCB in hand
Testing & Validation: run spec tests and record results.
Integration with Subsystems: mount, wire, and verify end-to-end alerts.
Documentation & Review: update ICD/FSR/BoM to match the build.
Final Adjustments & Submission: fix small issues and submit.

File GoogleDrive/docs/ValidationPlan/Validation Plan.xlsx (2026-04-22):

Paragraph # | Test Name | Success Criteria | Methodology | Status | Responsible Engineer |  | Paragraph # | Test Name | Success Criteria | Methodology | Status | Responsible Engineer
3.2.1.1. | Fall Detection Accuracy | The chosen ML model must report falls within an accuracy range of a minimum of 90% | The RADIAN Data subteam lead will continuously check accuracy of chosen ML model using Python code and visual confirmation. | Not Completed | Matthew | Currently working on increasing accuracy | 3.2.1.1. | Fall Detection Accuracy | The chosen ML model must report falls within an accuracy range of a minimum of 90% | The RADIAN Data subteam lead will continuously check accuracy of chosen ML model using Python code and visual confirmation. | Not Completed | Matthew
3.2.1.2. | Detection latency | The Raspberry Pi 3 is able to communicate with the RADIAN application within ~8 seconds of detected fall. | The RADIAN group will send positive fall alert from the Raspberry Pi 3 to the Gotify server. The server will then send the alert to the RADIAN application to alert the caregiver. This process will be timed using the internal clock of the Raspberry Pi 3 as well as a physical stopwatch to ensure the notification was sent with ~5 seconds of the fall. | Pass | Matthew & Mitch |  | 3.2.1.3. | Battery LIfe | The RADIAN system must operate for 4 hours with normal operation (People going in and out of a room, and two falls detected). | Physical team measures runtime on battery at average load with two scripted fall detection, pass if ≥ 4 h | Not Completed | Wyatt
3.2.1.3. | Battery LIfe | The RADIAN system must operate for 4 hours with normal operation (People going in and out of a room, and two falls detected). | Physical team measures runtime on battery at average load with two scripted fall detection, pass if ≥ 4 h | Not Completed | Wyatt | Tomorrow | 3.2.1.4. | Communication Reliability | The RADIAN application must work within a ~200 meter radius from the system and will send a alert with a minimum of 95% success rate. | The RADIAN group will have on member stand outside of the ~200 meter radius and inside the ~200 meter radius to test if a push notification was received from the Raspberry Pi 3. There will also be a certain number of scripted notifications and log the amount of received notifications. | Not Completed | Matthew & Mitch
3.2.1.4. | Communication Reliability | The RADIAN application must work within a ~200 meter radius from the system and will send a alert with a minimum of 95% success rate. | The RADIAN group will have on member stand outside of the ~200 meter radius and inside the ~200 meter radius to test if a push notification was received from the Raspberry Pi 3. There will also be a certain number of scripted notifications and log the amount of received notifications. | Not Completed | Matthew & Mitch | Planned with new server | 3.2.1.6. | Autonomous Operation | The RADIAN system shall operate autonomously with minimal user interaction. | Trigger a fall event and verify the app gets the notification and then trigger another fall event 1 hour after the first one was detected. | Not Completed | Mitch
3.2.1.5. | Local Alert Functionality | Audible alarm at 70 dB at 1m. | Use SPL meter at 1m, trigger alert, record dB. | Pass | Wyatt |  | 3.2.3.1.1 | Power Consumption | The peak power draw of the system shall not exceed 8 watts. | Run worst case (Pi CPU load + radar high duty) and measure 5V current and calculate P = VI. | Not Completed | Wyatt
3.2.1.6. | Autonomous Operation | The RADIAN system shall operate autonomously with minimal user interaction. | Trigger a fall event and verify the app gets the notification and then trigger another fall event 1 hour after the first one was detected. | Pass | Mitch | This will be a final test, all that needs to be done is start it on boot | 3.2.4.1 | Thermal | The RADIAN system will be capable of operating between 50 °F and 80 °F | Room/chamber test from 50 °F and 80 °F, log temps and performance. | Not Completed | RADIAN Group
3.2.2.1. | Radar Scan Area | Radar module effectively monitors a 20-30 square meters when mounted. | Mount radar module at a 45 degree downward tilt in a controlled 25 square meter test area. Place reflective targets or human subjects at multiple locations within test area. record detection coverage. | Pass | Mitch
3.2.2.2. | Mass | RADIAN system must be less than 0.8 kilograms. | Weigh system with a scale once final design is Pass. | Pass | Wyatt
3.2.2.3. | Volume Envelope | RADIAN system must be less than or equal to 14 in x 8 in x 5 in. | Measure radome using tape measure. | Pass | Wyatt
3.2.3.1.1 | Power Consumption | The peak power draw of the system shall not exceed 8 watts. | Run worst case (Pi CPU load + radar high duty) and measure 5V current and calculate P = VI. | Not Completed | Wyatt | Tomorrow
3.2.3.1.2 | Input Voltage Level | System operate at 5.0V. | Apply 5.0V supply and measure the voltage at Pi and radar connectors. | Pass | RADIAN Group
3.2.3.1.3 | Power Supply Output Ripple | Output ripple voltage shall not exceed 50 mV Pk-Pk across all load conditions (0.5 A – 2.5 A). | Applied 0.5 A, 1.0 A, 1.5 A, 2.0 A, and 2.5 A loads to the 5V output. Measured ripple with an oscilloscope (AC-coupled, 20 MHz BW limit). Recorded Pk-Pk ripple at each load point. | Pass | Wyatt
3.2.3.1.4 | Pi + Radar UART Communication Verification | Raspberry Pi 3B+ shall successfully establish UART communication with the IWR6843ISK radar at 115200 baud and execute sensorStop/sensorStart commands without error. Supply voltage shall read ≥4.9 V under combined radar + network load. | Powered system with Pi + radar + Wi-Fi active (not full CPU load). Measured supply voltage with multimeter. Connected via minicom (-D /dev/ttyUSB0 -b 115200) and issued sensorStop then sensorStart. Verified 'Done' response for each command. | Pass | Wyatt
3.2.3.1.5 | Power Supply Stability Under CPU Stress | The 5V power supply shall remain stable (no voltage instability or resets) while the Raspberry Pi executes a full CPU stress test at 100% utilization on all 4 cores for 60 seconds. | Ran 4 parallel CPU stress processes using: `for i in 1 2 3 4; do yes > /dev/null & done; sleep 60; killall yes`. Monitored system for voltage instability, thermal throttling, or unexpected resets during 60-second duration. | Pass | Wyatt
3.2.3.1.6 | MP2615 2S Battery Charger Validation | MP2615 charger shall deliver charge current to the 2S Li-ion pack and increase pack voltage over time at the expected CC/CV profile without fault. | Monitored pack voltage and charge current vs. time using data logger over 15-minute interval. Recorded start voltage, end voltage, delta voltage, elapsed time, and average charge current. | Pass | Wyatt
3.2.3.1.7 | Buck Converter Load Regulation | Output voltage (Vout) shall remain at or above 4.63 V across all load conditions from 0.1 A to 2.5 A. | Connected a programmable electronic load to the 5V output rail. Swept load current from 0.1 A to 2.5 A in steps (0.10, 0.25, 0.50, 1.00, 1.30, 1.50, 1.70, 1.80, 1.90, 2.00, 2.10, 2.20, 2.50 A). Recorded Vout at each step. Plotted Vout vs. Iout curve and verified minimum voltage above 4.63 V at full load. | Pass | Wyatt
3.2.3.2.1 | Data Output | App interface accepts/decods fall events from Gotifiy Cloud server. | Send test events over REST/WebSocket and confirm app renders a notification. | Pass | Matthew & Mitch
3.2.3.2.3 | Wireless Communication Output | Raspberry Pi 3 is able to communicate to the RADIAN application at an accuracy rate of 98%. | The RADIAN team will send a variety of notifications to the RADIAN application, both falls and not falls, and record the accuracy of each event occurring on the RADIAN application | Pass | Matthew & Mitch
3.2.4.1 | Thermal | The RADIAN system will be capable of operating between 50 °F and 80 °F | Room/chamber test from 50 °F and 80 °F, log temps and performance. | Pass | RADIAN Group | Later
4.1 | Wi-Fi Connection | The Raspberry Pi 3 connects to a specified Wi-Fi network and transmits a REST POST notification to the Gotify cloud server. | Monitor network status using Pi's terminal or a network monitor. Confirm a successful REST POST and verify message receipt on the Gotify server. | Pass | Matthew & Mitch
4.2 | Wi-Fi or Cellular Data Connection | The caregiver's smartphone receives the RADIAN push notification within 5 seconds of it being sent by the Gotify server. | Trigger a test alert from the RADIAN device. Observe the phone's receipt of the notification and record delivery times. | Pass | Matthew & Mitch

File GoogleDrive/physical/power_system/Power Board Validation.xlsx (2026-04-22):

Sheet: Sheet1
 | Section | Test ID | Title | Purpose | Setup | Procedure | Pass/Expected | Evidence | Comments
TRUE | Pre-Fab | PF-01 | Schematic ERC/DRC sign-off | Catch obvious logic/net/power errors before build | CAD open; latest schematic/PCB; BOM Rev | Run ERC/DRC; resolve all errors; waivers documented | 0 ERC errors; 0 DRC errors or documented waivers | DRC/ERC Reports (https://drive.google.com/drive/folders/1iNFlbQl2YLbyLB7u8HyMmjH933zTsPnf?usp=sharing) | ERC Report has error due to labeling of charging IC output and boost IC input. Wavied.
TRUE | Pre-Fab | PF-03 | Footprint-Symbol-BOM cross-check | Verify pin-maps, rotations, package codes | Datasheets for charger IC, boost IC, holders, connectors | For each major part, confirm land pattern, pin 1, exposed pad mapping | All parts match mfr drawings; exposed pads tied correctly | Datasheets (https://drive.google.com/drive/folders/11upym-puAl1cld4cLe2gwy6524rAEsh3?usp=sharing)
TRUE | Pre-Fab | PF-04 | Power tree review | Confirm voltage/current budgets | Design power spreadsheet | Sum max loads; check charger/boost ratings and copper widths | Margins >=20% current on traces & ICs | WEBENCH-Simulations (https://drive.google.com/drive/folders/1Aeil7xbZGoq1_p3Av18_y_sAaHbV3udk?usp=sharing)
TRUE | Bare PCB | BP-01 | Visual & dimensional check | Ensure board meets fab drawing | Calipers; gerbers; fab drawing | Measure X/Y, hole diameters, slot sizes; inspect silks/masks | Within +/-0.2 mm on critical; silkscreen legible; mask not on pads | Dimensions (https://drive.google.com/drive/folders/1flPjRwMKzKuDPxFuRxUfQy1xk0cDq3LM?usp=sharing)
TRUE | Bare PCB | BP-03 | Test coupon solderability | Check finish quality | Solder iron, flux, solder wire | Tin a coupon/pad; inspect wetting | Smooth, shiny fillet; no dewetting | Solderability (https://drive.google.com/drive/folders/1TbItnK6alCjCVij-KSdQ1mVX06zX4quY?usp=sharing)
TRUE | Bare PCB | BP-04 | Fit check: 18650 holders & connectors | Verify mechanicals before reflow | Actual holders, barrel/USB, standoffs | Place parts; confirm clearance, hole alignment | All parts seat flat; holes align | Fit-Check (https://drive.google.com/drive/folders/15phb4OZOXeoZFne7VbhTZ1_xg4iPwbYc?usp=sharing)
TRUE | Assembly | AS-01 | Paste application / reflow profile | Right amount of paste and thermal profile | Stencil or syringe; reflow oven; thermocouple | Follow vendor profile; record soak/peak/time-above-liquidus | Within datasheet limits for all ICs | Datasheets (https://drive.google.com/drive/folders/11upym-puAl1cld4cLe2gwy6524rAEsh3?usp=sharing)
TRUE | Assembly | AS-02 | Microscope inspection | Find bridges, voids, tombstones | Microscope 10-40x | Scan all IC pins, passives, thermal pads | No bridges/voids >25% on EP; good fillets | Solder-Inspection (https://drive.google.com/drive/folders/1e1JE0yM9B_PRkSW65exP14hIzsisSlTu?usp=sharing)
TRUE | Assembly | AS-03 | Polarity/orientation | Avoid reverse installs | Datasheets; silksheet | Verify diodes, LEDs, electrolytics, IC pin-1 | All correct | Results (https://docs.google.com/document/d/1Rsxe0h0p1vR9lo6zyCx7KQMutvcouBBnyb1vLPM-nrk/edit?usp=sharing)
TRUE | Pre-Power | PP-01 | Resistance-to-ground check | Detect gross shorts | DMM | Measure R from +BAT, +SYS, +5V to GND | Typically >100 Ohm; note inrush from caps | Results (https://docs.google.com/document/d/1ejzDmm1LWvj84aBiIj_O4qnVvOLoMmbNEMyHYooy1qE/edit?usp=sharing)
TRUE | Pre-Power | PP-02 | Bench supply limited power-on (no battery) | Safe first power | Bench supply 5-6 V, 100 mA limit; scope | Feed VIN for charger and BAT; observe current draw & hot spots | Idle current <50 mA (depends design); no hotspots | 0.01A
TRUE | Pre-Power | PP-03 | Key node DC sanity | Verify rails exist | DMM | Measure VIN, BAT nodes (BAT will float) | VIN, VOUT, CHARGE | 3.75V, 5.02V
TRUE | Charger | CH-01 | Emulate battery with bench supply | Validate charger without cells | Bench supply set to 3.7 V; 2 A limit; connect to BAT node | Power VIN=5 V; vary BAT 3.0-4.2 V; monitor CHG LED/STAT pins & SYS | Chg current follows config; taper near 4.2 V; STAT behavior matches DS
TRUE | Charger | CH-02 | Charge profile with real cell | Verify CC/CV and termination | One 18650 w/ inline current sense | Start at ~3.6 V cell; log Vbat and time; until termination | CC to IREG, then CV to 4.20+/-0.05 V; terminate at Iterm; no overtemp
TRUE | Battery | BT-01 | Cell sharing check | Ensure no large equalization surge | Two cells at 4.0 V & 3.8 V; 0.05 Ohm sense in series with each | Connect both via holders; record equalization current | Peak <1.5 A and decays quickly (adjust per design)
FALSE | Battery | BT-02 | Protection IC trip points (DW01A+8205A) | Confirm OVP/UVP/OCP | Programmable supply/load; scope | Sweep Vbat up to OVP; down to UVP; step load to OCP | Trips near DS: OVP ~4.3 V; UVP ~2.4-2.5 V; OCP ~3-6 A | Tripping too high
TRUE | Boost | BS-01 | No-load output | Baseline regulation | Battery at 3.7 V (bench or real) | Power board; measure Vout no-load | Vout 5.0 V +/-2% | 5.02V
TRUE | Boost | BS-02 | Load regulation sweep | Voltage vs load | Electronic load 0-Imax | Step 0 -> 0.1 A -> 0.5 A -> 1 A -> Imax | Delta V <5% over range; no oscillation
FALSE | Boost | BS-03 | Efficiency vs load | Thermal/power performance | Measure Vin/Vout/Iin/Iout | Sweep loads; compute Î· | Meets design targets (e.g., >=90% mid-load)
TRUE | Boost | BS-04 | Startup under load | Soft-start behavior | Set load 0.5xImax; power input | Capture Vout/Vin/Iin during start | No overshoot >10%; starts reliably | V_out = 4.9V
TRUE | Boost | BS-06 | Output ripple | Compliance with spec | Scope 20 MHz limit; tip-and-barrel probe | Measure ripple at I=0.5xImax | pp ripple within datasheet limits (e.g., <50 mVpp)
FALSE | System | SY-02 | Thermal at worst-case load | Hot spot identification | IR camera or thermocouples; enclosure if applicable | Run Imax for 20 min at 25 degC; repeat at 40 degC ambient | Tj estimate within limits; case <85 degC

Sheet: Sheet3
Test | Description | System | Status
WEBENCH Design Simulation | Steady-state, startup, load-transient, and input-transient simulations validate TPS61022 component choices and operating margins | Boost | Completed
ERC/DRC Sign-off | Run schematic/PCB ERC/DRC and waive labeling issue on charger/boost connection | Power Board | Completed
Footprint/BOM Cross-Check | Verify charger, boost, holders, and connector footprints and pin mappings against datasheets | Power Board | Completed
Power Tree Review | Review voltage and current budgets against loads and IC ratings. | Power Board | Completed
Visual & Dimensional Check | Inspect bare PCB size, hole locations, silkscreen, and solder mask vs. fab drawing | Power Board | Completed
Solderability Check | Test pad finish quality by tinning a coupon/pad and inspecting wetting | Power Board | Completed
Fit Check: 18650 Holders & Connectors | Verify 18650 holders, barrel jack, and connectors seat flat and align with holes before reflow | Power Board | Completed
Reflow Profile Check | Apply paste and reflow; confirm thermal profile is within datasheet limits for ICs | Assembly | Completed
Microscope Inspection | Inspect IC pins and passives for bridges, voids, tombstones, and poor fillets | Assembly | Completed
Polarity/Orientation | Check diodes, LEDs, electrolytics, and IC pin 1 orientation vs. silkscreen | Assembly | Completed
Resistance-to-GND Check | Measure resistance from +BAT and +5 V rails to GND to catch gross shorts before power-on | Power Board | Completed
Limited Bench Power-On | Power VIN from bench supply with current limit; confirm reasonable idle current and no hot spots | Charger/Boost | Completed
Key Node DC Sanity | Check VIN, battery node, and 5 V rail voltages with no load | Power Board | Completed
Charger Bench Emulation | Emulate battery with bench supply; verify TP4056 charge behavior and status pins vs. datasheet | Charger | Completed
Single-Cell Charge Profile | Charge 18650 cell; log battery voltage over time to confirm CC/CV behavior and termination | Charger | Completed
Dual-Cell Pack Charge Curve | Charge 2×18650 pack; record pack voltage vs. time | Charger | Completed
Charge + Boost Operation | Run TP4056 charging while boost converter supplies 5 V rail; check for heating or instability | System | Completed
No-Load Output | Measure 5 V rail at no load; verify approximately 5.0 V regulation | Boost | Completed
Efficiency vs Load | Measure Vin/Vout/Iin/Iout and compute efficiency vs load | Boost | Not performed (Future)
Startup Under Load | Verify boost circuit can start up under load | Boost | Completed
Quiescent Current | Test full-board standby current for battery-life estimation | System | Not performed (Future)
Thermal at Worst-Case Load | Run near maximum load and log board hot-spot temperatures | System | Not performed (Future)
Raspberry Pi Load Test | Power Raspberry Pi 3 from board; verify successful boot and stable ~4.9–5.0 V rail | System | Completed
UART Communication Integrity Test | Radar correctly transmits binary TLV packets and Python script decodes them | Radar | Completed
Point Cloud Accuracy Test (static target) | Radar accurately reports x, y, z coordinates of stationary object | Radar | Completed
Point Cloud Accuracy Test (moving target/velocity) | Radar accurately reports Doppler-based velocity estimation | Radar | Completed
Multiple Object Detection Test | Radar can detect more than one target simultaneously | Radar | Completed
Configure File Test (.cfg integration) | Ensure custom configurations change radar behavior | Radar | Completed
Real Time Terminal Display Test | Python file displays live point cloud data without delay or crash | Radar | Completed
App Navigation Test | All tabs function and route correctly | App | Completed
Alert Simulation Test | Fall simulation button triggers critical alert logic | App | Completed
Settings and Server Connection Test | Validate server connection workflow | App | Completed
Gotify Push Notification Test | App receives live notifications from server | App | Completed
Weekly Fall Log Generation Test | Validate automatic weekly log creation | App | Completed
Data Persistence Test | Fall logs persist after app close/restart | App | Completed
UI Responsiveness Test | App layout works on multiple screen sizes | App | Completed
Pi–Server Connectivity Test | Verify Raspberry Pi can reach the laptop/host running Gotify via local IP (ping test) | Notification Server | Completed
Gotify Installation Verification | Confirm Gotify server is installed on the Raspberry Pi by inspecting the pip list and verifying the package | Notification Server | Completed
Gotify UI and Token Setup | Test Gotify UI in a web browser via the laptop IP address and create/share the application token for RADIAN | Notification Server | Completed
Basic Message Publishing | Test Python script sending a “Hello World” message via HTTP POST from the Pi to Gotify and verify it appears in the Gotify UI | Notification Server | Completed
Invalid Token Handling | Test server behavior with an incorrect app token and confirm an error is reported and the message is not accepted | Notification Server | Completed
Repeated Message Stability | Test repeated message sends in rapid succession from Pi to Gotify and verify no alerts are dropped | Notification Server | Completed
Server Restart Recovery | Restart Gotify server and confirm it resumes normal operation and can receive new messages | Notification Server | Completed
End-to-End Alert Path Sanity | Check that the path AI → Python script → Gotify server works in the lab setup with test alerts | Notification Server | Completed
Model Training & Confusion Matrix Check | Verify the random forest classifier correctly separates static vs dynamic motion; inspect accuracy and confusion matrix on synthetic data | Artificial Intelligence | Completed
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

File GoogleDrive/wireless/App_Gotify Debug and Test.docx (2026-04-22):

irThis is our first testing of the gotify testing between the pi and the mobile app:

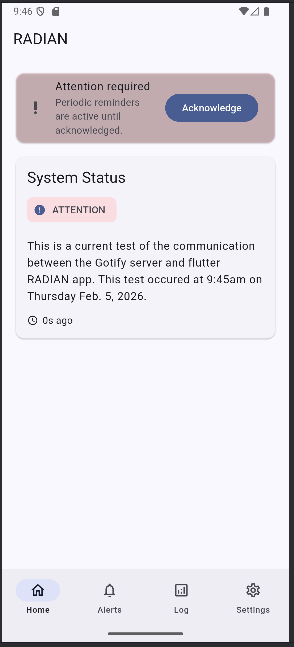
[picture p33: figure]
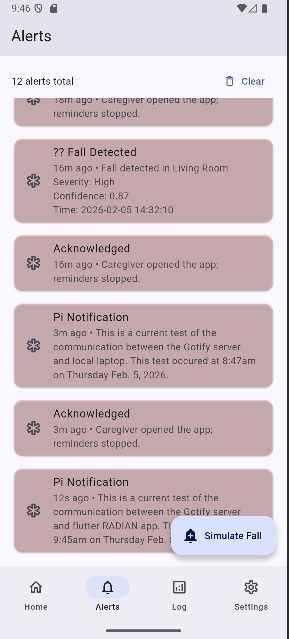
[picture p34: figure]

What needs to be debugged on the app:

- Alerts are coming through the alert tab bottom to top, needs to be top to bottom
- Need to get rid of the internal simulate fall alerts now that we have connected the gotify server
- The alerts coming from the gotify server are not being uploaded into the fall log
- In the settings change “app token” to “client token”
- Change the “Gotify Connection” box in the settings tab to collapse when the emulator has connected to the server, as a sign of connection
- Any place where there is a “____ ago”, change it so that it updates with the time instead of updating the time that has past when you leave the tab and go back to that tab
- If it already isnt in the code, add code so that when there is a fall alert, have the alert make note of what kind of fall it was and where, because the data will already be classified this way

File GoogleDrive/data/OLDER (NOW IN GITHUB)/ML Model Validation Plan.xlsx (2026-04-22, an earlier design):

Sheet: ML Model Plan
Stage | Category | Validation Item | Description | Expected Outcome | Validation Metric | Pass/Fail | Notes
Data Validation | Schema | Verify schema consistency | All radar frames and IMU signals have identical column names, data types, and sampling rate | No schema mismatches | # of schema errors = 0 | ☐
Data Validation | Missing Data | Check for missing or NaN values | Ensure no missing timestamps or NaN amplitude values | < 1% missing per signal | % missing values | ☐
Data Validation | Range Check | Validate value bounds | Doppler, range, and power values fall within sensor limits | 0 out-of-range values | Count of invalid samples | ☐
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

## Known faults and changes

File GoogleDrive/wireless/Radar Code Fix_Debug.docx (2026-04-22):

What to fix/debugg in mmwave_run.py (simply clean up code to get better data for integration)

-timestamp at each frame (change to timestamp to radars timestamp)

-confidence scale

-look into making data better (and output) for last known center when tracking a “person”

Debug checklist:

- output hygiene
  - STDOUT = NDJSON only ✔
  - STDERR = debug only ✔
  - One JSON object per frame ✔
- State correctness
  - reset ‘person’ every frame
  - center=null when num_points==0
  - No stale data reuse
- Contract clarity
  - Document timestamp units
  - Document coordinate frame
  - Document confidence meaning

Output:

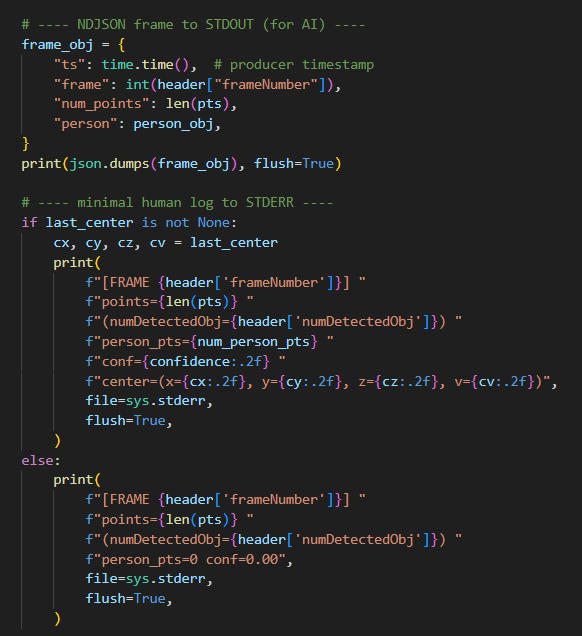
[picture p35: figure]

To explain the output, there are two different outputs that are going to the terminal. The first ‘line’ going to the terminal is the NDJSON frame, this is where you will see this:

The ML will be able to read the data (from left to right), the timestamp, the frame number, number of points, the confidence interval, and if there is someone being tracked, will also see x,y,z positioning and velocity.

The second output, ‘human log to STDERR,’ will be the second ‘line’ in the terminal following the NDJSON frame, where it’ll look like this:

This output is already coded to not be sent to the raspberry pi. We know this because in the if/else statement above the line ‘file=sys.stderr’ will take this line of data and send it to standard error (STDERR).

So yes, because the output in the terminal looks like there are two different lines of data being sent to the pi, but that is actually not the case. Only the first line of data will be sent to the ML model and the second line is just for use to see when we run the radar through the terminal.

Also, not sure if you are asking yourself this but i needed clarification so i thought id share incase you did too. The ‘NDJSON frame to STDOUT (for AI)’ output is a NDJSON stream. Each line in this stream is a NDJSON record/line, and each NDJSON record/line is a JSON object. So yes you are getting a JSON object at each frame. NDJSON is just used so that each frame is an individual object, otherwise with just JSON each frame would be put into a single array, which would cause you to need to parse each frame one by one to get the data at each frame.

Tracking/Memory:

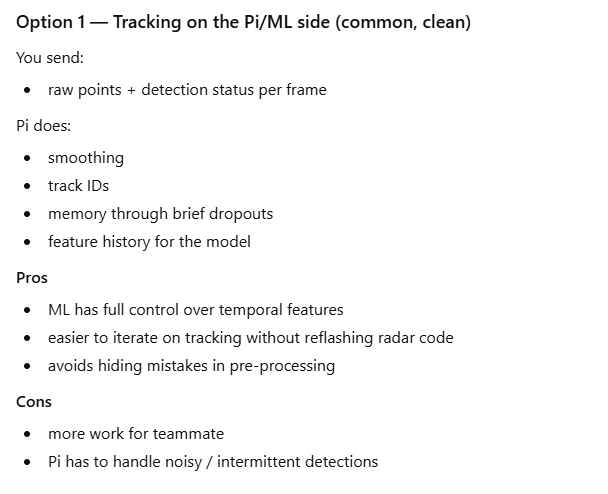
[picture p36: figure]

going with this option (unless something changes in the future)

Decided to have the radar be used for detection only as well as not tracking a ‘center’ of the object (keeping all the points detected on the object).

Because I am no longer computing a center from all the points detected on a person, each json that is being sent to the pi will be an array of multiple points that are being detected on a person. Therefore, from one json to the next may or may not have the same number of points being detected on a person. Here is what the json could look like:

"person": {

"num_points": 6,

"confidence": 0.6,

"points": [

{"x":0.42,"y":1.03,"z":0.06,"v":0.31},

{"x":0.45,"y":1.09,"z":0.05,"v":0.29},

{"x":0.39,"y":0.97,"z":0.08,"v":0.34}

]

}

Also the benefit of doing the radar data processing being just detection it’ll preserve the shape, height distribution, and velocity distribution that will make the ML model easier to infer posture, collapse, and motion patterns.

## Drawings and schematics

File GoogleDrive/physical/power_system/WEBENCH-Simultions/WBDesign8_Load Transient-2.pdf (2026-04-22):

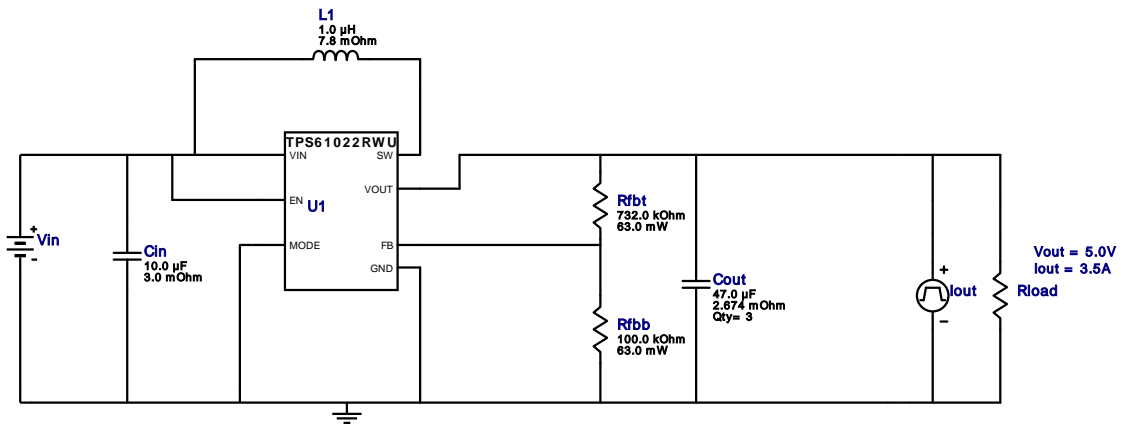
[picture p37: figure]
Vout = 5.0V Iout = 3.5A; TPS6 1 0 2 2 RW U; GND; VOUT; MODE; VIN; Cin 10.0 µF 3.0 m Ohm; Rfbb 100.0 kOhm 63.0 m W; Cout 47.0 µF 2.674 m Ohm Qty= 3; Rfbt 732.0 kOhm 63.0 m W; L1 1.0 µH 7.8 m Ohm; Vin; Iout; Rload

Copyright © 2025, Texas Instruments Incorporated | 1 | ti.com/webench

WEBENCH®
Design Report TPS61022RWUR : TPS61022RWUR 2.5V-4.2V to 5.00V @ 3.5A November 3, 2025 12:14:15 GMT-06:00

## WEBENCH ® Design Report

Design : 8 TPS61022RWUR
TPS61022RWUR 2.5V-4.2V to 5.00V @ 3.5A

VinMin = 2.5V
VinMax = 4.2V
Vout = 5.0V
Iout = 3.5A

Device = TPS61022RWUR
Topology = Boost_PassThrough Created = 2025-10-01 17:10:30.940 BOM Cost = $2.19
BOM Count = 8
Total Pd = 1.61W

### Design Alerts

Component Selection Information
1. The TPS61022 Device will operate in Pass-Through mode when Vin is greater than Vout. In Pass-Through mode, Vout is not regulated to the set Vout, instead Vout is Vin with the drop across the FETï¿½s on-resistance and the DCR of the inductor. 2. This is a Boost Converter with 0.5V ultra-low input voltage. 3. The efficiency validation is done only for FPWM mode. Charts may be inaccurate for AutoMode at light loads and hence they are disabled for light loads.

## Electrical BOM

Name | Manufacturer | Part Number | Properties | Qty Price | Footprint
Cin | Kemet | C0805C106K8PACTU (http://capacitoredge.kemet.com/capedge2/DataSheet/Datasheet%2DC0805C106K8PACTU.pdf?pn%3DC0805C106K8PACTU) Series= X5R | Cap= 10.0 uF ESR= 3.0 mOhm VDC= 10.0 V IRMS= 11.43 A
1 | $0.03
| | | | | 0805 7 mm²
Cout | Taiyo Yuden | MSASL21GBB5476MTNA01 (https://ds.yuden.co.jp/TYCOMPAS/ut/detail?pn%3DMSASL21GBB5476MTNA01%26u%3DM) Series= X5R

Cap= 47.0 uF
ESR= 2.674 mOhm
VDC= 10.0 V
IRMS= 3.1668 A

3 $0.26
0805 7 mm²
L1 | TDK | SPM6530T-1R0M120 (http://product.tdk.com/inductor/ind/en/documents/inductor%5Fcommercial%5Fpower%5Fspm%5Fen.pdf) | L= 1.0 µH 7.8 mOhm | 1 | $0.59

SPM6530 77 mm²
Rfbb | Vishay-Dale | CRCW0402100KFKED (http://www.vishay.com/docs/20035/dcrcwe3.pdf) Series= CRCW..e3 | Res= 100.0 kOhm Power= 63.0 mW Tolerance= 1.0% | 1 | $0.01
0402 3 mm²
Rfbt | Vishay-Dale | CRCW0402732KFKED (http://www.vishay.com/docs/20035/dcrcwe3.pdf) Series= CRCW..e3 | Res= 732.0 kOhm Power= 63.0 mW Tolerance= 1.0% | 1 | $0.01
0402 3 mm²
U1 | Texas Instruments | TPS61022RWUR (http://www.ti.com/product/TPS61022) | Switcher | 1 | $0.75
RWU0007A 9 mm²

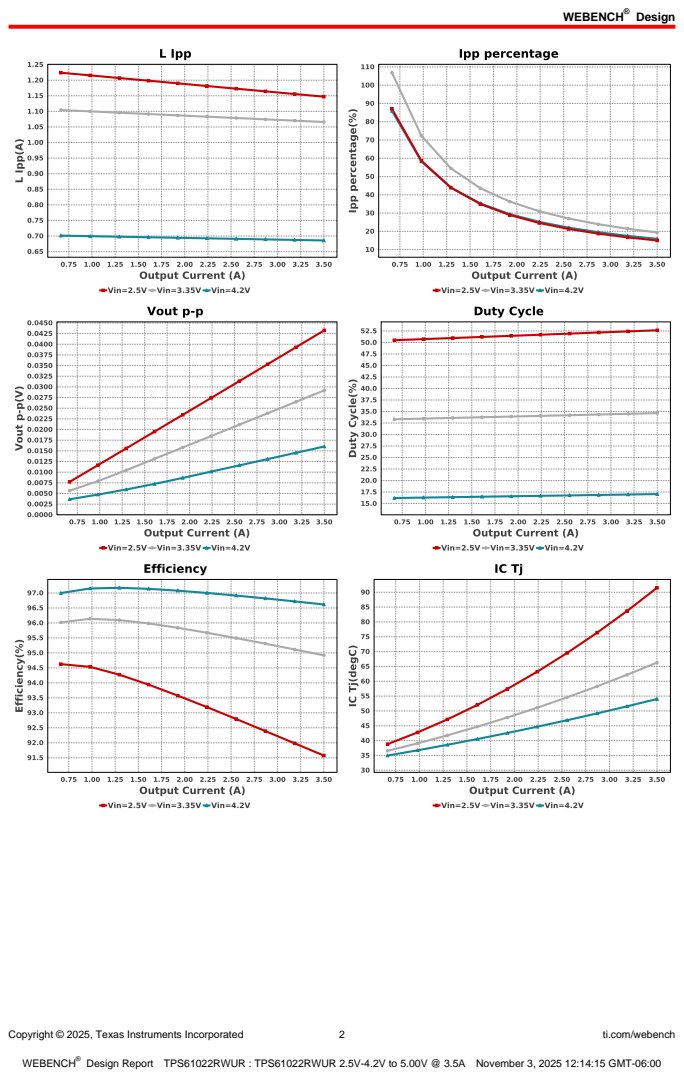
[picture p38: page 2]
Design; Copyright © 2025, Texas Instruments Incorporated; ti.com/webench

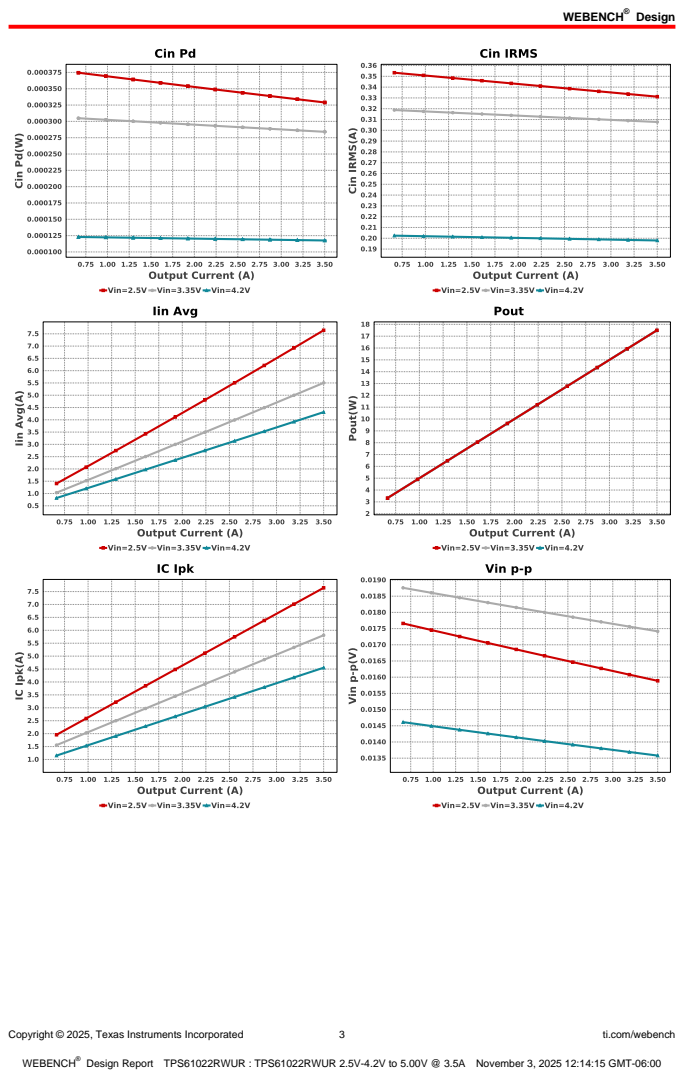
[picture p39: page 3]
Copyright © 2025, Texas Instruments Incorporated; ti.com/webench

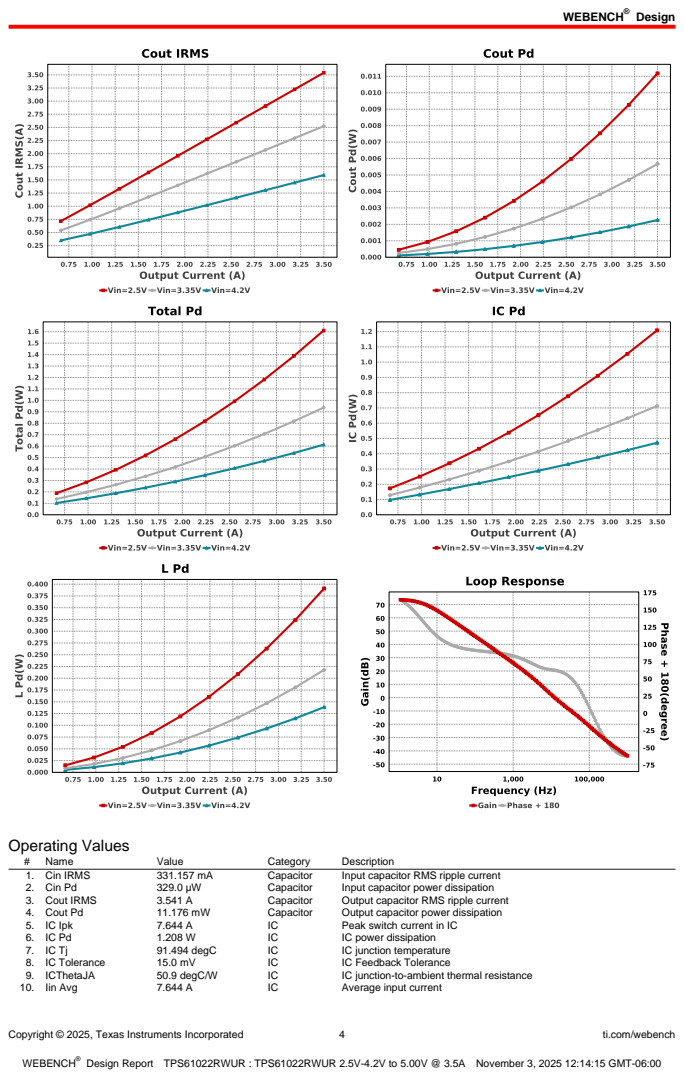
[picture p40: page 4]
Copyright © 2025, Texas Instruments Incorporated; ti.com/webench; Operating Values; Name; Value; Category; Description; 1. Cin IRMS; Capacitor; Input capacitor RMS ripple current; 2. Cin Pd; Input capacitor power dissipation; 3. Cout IRMS; Output capacitor RMS ripple current; 4. Cout Pd; Output capacitor power dissipation; 5. IC Ipk; Peak switch current in IC; IC power dissipation; 91.494 degC; IC junction temperature; 8. IC Tolerance; IC Feedback Tolerance; 9. ICThetaJA; 50.9 degC/W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

Copyright © 2025, Texas Instruments Incorporated | 5 | ti.com/webench
# | Name | Value | Category | Description

11. Ipp percentage | 15.007 % | Inductor | Inductor ripple current percentage (with respect to average inductor
| | | | current)
12. L Ipp | 1.147 A | Inductor | Peak-to-peak inductor ripple current
13. L Pd | 390.82 mW | Inductor | Inductor power dissipation
14. Cin Pd | 329.0 µW | Power | Input capacitor power dissipation
15. Cout Pd | 11.176 mW | Power | Output capacitor power dissipation
16. IC Pd | 1.208 W | Power | IC power dissipation
17. L Pd | 390.82 mW | Power | Inductor power dissipation
18. Total Pd | 1.61 W | Power | Total Power Dissipation
19. BOM Count | 8 | System
| | | Information | Total Design BOM count
20. Cross Freq | 8.004 kHz | System
| | | Information | Bode plot crossover frequency
21. Duty Cycle | 52.652 % | System
| | | Information | Duty cycle
22. Efficiency | 91.573 % | System
| | | Information | Steady state efficiency
23. FootPrint | 119.0 mm² | System
| | | Information | Total Foot Print Area of BOM components
24. Frequency | 1.06 MHz | System
| | | Information | Switching frequency
25. Gain Marg | -18.07 dB | System
| | | Information | Bode Plot Gain Margin
26. Iout | 3.5 A | System
| | | Information | Iout operating point
27. Low Freq Gain | 68.691 dB | System
| | | Information | Gain at 1Hz
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

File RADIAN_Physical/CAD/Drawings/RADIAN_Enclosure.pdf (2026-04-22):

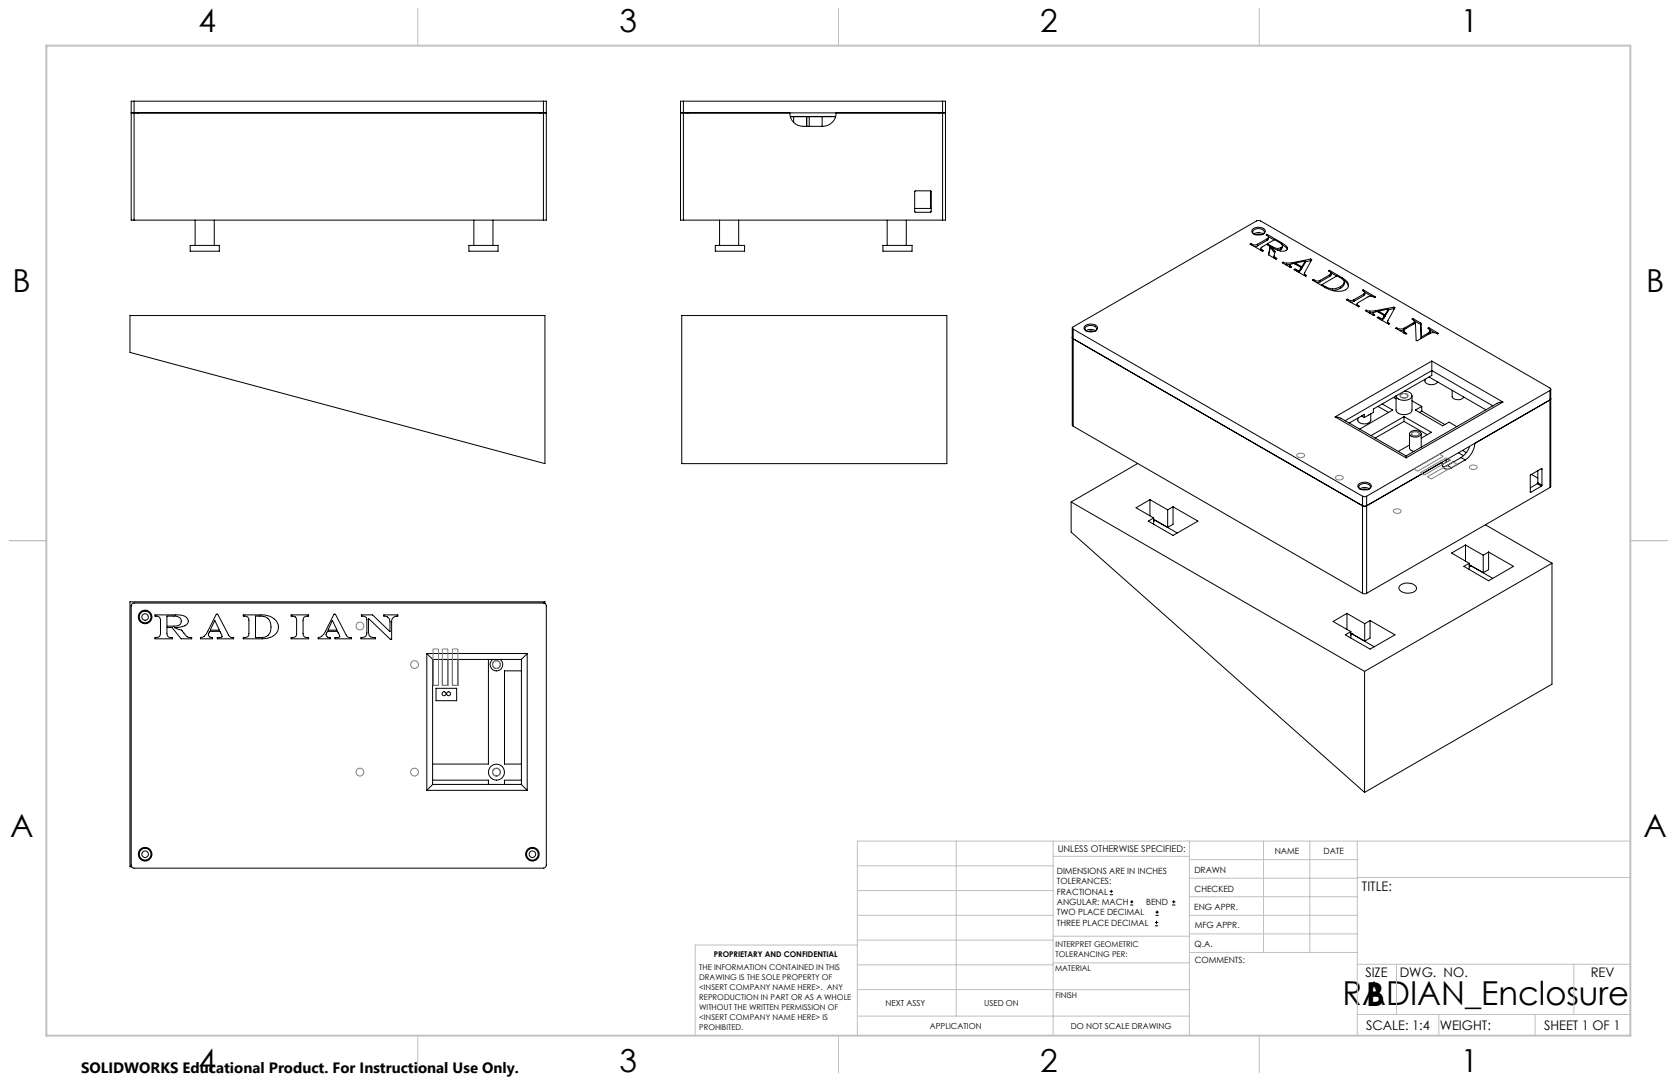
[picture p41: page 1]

UNLESS OTHERWISE SPECIFIED: | | NAME | DATE
DIMENSIONS ARE IN INCHES TOLERANCES: FRACTIONAL ANGULAR: MACH BEND TWO PLACE DECIMAL THREE PLACE DECIMAL | DRAWN

CHECKED | | | TITLE:

ENG APPR.
MFG APPR.

INTERPRET GEOMETRIC TOLERANCING PER: | Q.A.
MATERIAL | RADIAN_Enclosure | SIZE B | DWG. NO. | REV

PROPRIETARY AND CONFIDENTIAL
THE INFORMATION CONTAINED IN THIS
DRAWING IS THE SOLE PROPERTY OF
<INSERT COMPANY NAME HERE>. ANY
REPRODUCTION IN PART OR AS A WHOLE
WITHOUT THE WRITTEN PERMISSION OF
<INSERT COMPANY NAME HERE> IS
PROHIBITED.

NEXT ASSY | USED ON | FINISH

APPLICATION | DO NOT SCALE DRAWING | | SCALE: 1:4 | WEIGHT: | SHEET 1 OF 1

SOLIDWORKS Educational Product. For Instructional Use Only.

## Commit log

2025-11-11 Update fall_detection_simulation.py
    Comparing the AVERAGE of the last few frames before and after the fall.
2025-11-25 Create movement_edgecase_generator.py
    Adding my edge case generator: sitting, bending over, kneeling, slow fall, trip recovery, crawling, pet walk, dropping objects, and a true hard fall.
2025-11-27 Update movement_edgecase_generator.py
    Adding more frames so we can see what the edge cases are doing
2025-12-01 Update movement_edgecase_generator.py
    Commenting out "slow_fall" and changing the edge case to "lying_down_slowly"
2025-12-01 Update even_more_robust_movement_classifier.py
    Changing the edge case from "slow_fall" to "lying_down_slowly"
2026-03-26 Uploading Claude code
    This code is from Wyatt to test deployment on the Raspberry Pi 3
2026-04-22 Revise README for clarity and accuracy
    Updated the README to clarify the enclosure description and removed outdated notes on hardware assembly. Adjusted key components table for accuracy.
2026-04-22 Rename Barrey Pack + Protection.SchDoc to Battery Pack + Protection.SchDoc
    [Battery Pack + Protection.SchDoc]
2026-04-22 Rename RADIAN_Physical/PCB/12V Input Protecion.SchDoc to RADIAN_Physical/PCB/Schematic/12V Input Protecion.SchDoc
    [12V Input Protecion.SchDoc]
2026-04-22 Rename RADIAN_Physical/PCB/Battery Pack + Protection.SchDoc to RADIAN_Physical/PCB/Schematic/Battery Pack + Protection.SchDoc
    [Battery Pack + Protection.SchDoc]
2026-04-22 Rename RADIAN_Physical/PCB/Buck Converter.SchDoc to RADIAN_Physical/PCB/Schematic/Buck Converter.SchDoc
    [Buck Converter.SchDoc]
2026-04-22 Rename RADIAN_Physical/PCB/Charger + PowerPath.SchDoc to RADIAN_Physical/PCB/Schematic/Charger + PowerPath.SchDoc
    [Charger + PowerPath.SchDoc]
2026-04-22 Rename RADIAN_Physical/PCB/USB Outputs.SchDoc to RADIAN_Physical/PCB/Schematic/USB Outputs.SchDoc
    [USB Outputs.SchDoc]
2026-04-22 Fix formatting in README.md for PCB section
2026-04-22 Remove assembly section from README
    Removed assembly section from the README file.
2026-04-22 Add all project files from Google Drive
    [Integration_Execution Timeline - 404.xlsx, Integration_Execution Timeline.xlsx, ML Model Validation Plan.xlsx, Power Board Validation.xlsx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]

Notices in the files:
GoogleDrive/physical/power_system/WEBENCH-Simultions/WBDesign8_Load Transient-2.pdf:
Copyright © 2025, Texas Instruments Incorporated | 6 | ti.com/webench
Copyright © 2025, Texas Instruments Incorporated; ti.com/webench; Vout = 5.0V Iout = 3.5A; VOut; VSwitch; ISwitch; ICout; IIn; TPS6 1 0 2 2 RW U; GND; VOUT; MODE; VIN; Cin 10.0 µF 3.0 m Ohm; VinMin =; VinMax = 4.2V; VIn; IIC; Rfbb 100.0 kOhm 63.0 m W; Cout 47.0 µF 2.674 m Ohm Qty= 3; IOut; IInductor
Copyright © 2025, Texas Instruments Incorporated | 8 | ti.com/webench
